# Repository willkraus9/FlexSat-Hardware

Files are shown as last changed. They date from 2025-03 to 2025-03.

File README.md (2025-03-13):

# FlexSat-Hardware

Happy FlexSat

## Hardware Setup:

* Obtain a battery (Turnigy 4S 14.8V 5000mAh, XT90 connector) for each motor

  * There should be another motor assembly in the lab for experiments with the two motor setup.
* Attach assembly to the mocap cage

  * Hold the aluminum plate perpendicular to a column in the mocap cage
  * Loosely fix the pipe clamps around the pipes
  * Tighten the pipe clamps with a Philips Head screwdriver
  * Make sure the final assembly is level, the final fit should be very snug

## Systems Overview:

### Motor Assembly

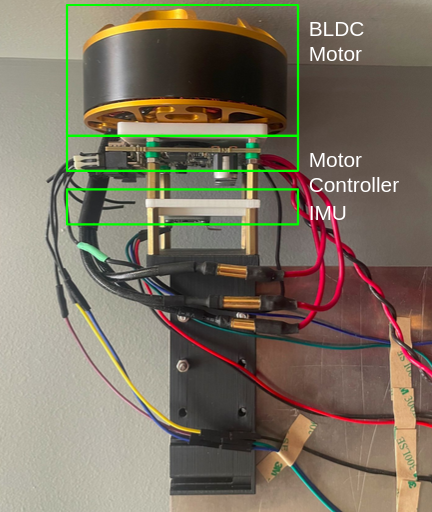
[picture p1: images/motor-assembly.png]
Motor Assembly


* The assembly is held together by M3 screws and standoffs. Reaching components for replacement (such as the motor) or manually adjusting (such as the IMUs) can be done with a small Philips screwdriver
* Ensure that the plastic spacers are attached such that the board does not short circuit due to how close metal components are to the PCB.

### Wiring Assembly

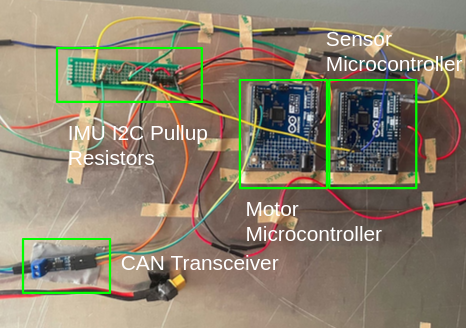
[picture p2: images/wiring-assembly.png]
Happy FlexSat


* Ensure the custom battery connector (XT90 -> XT60) is appropriately attached to the motor controller and the battery is secured
* Ensure the DuPont wires are attached to the microcontrollers and none have fallen out or bent
  * Pin connections can be found in the appropriate .ino files

## Initializing an Experiment:

1. Plug the motor(s) into battery power
2. Plug a computer into the motor controller using a USB type C cable
3. Initialize motor calibration as velocity control and testing using this link: https://gui.odriverobotics.com/

   * This should be done already and save over different sessions. However, testing the motors to check calibration ONLY would be helpful
   * More details for debugging: https://docs.odriverobotics.com/v/latest/interfaces/gui.html
4. Remove the USB cable from the motor controller
5. Attach two separate USB cables to the two separate microcontrollers
6. Test IMU data collection with the file FrequencyScheduler.ino
7. Test motor actuation with MotorTesterSingleArduino.ino, this should not rely on any IMU measurements.

## Running an Experiment:

1. Configure the scripts and USB connections

* MotorDualArduino.ino
* FrequencyScheduler.ino
* HW_Data_Collection.m

  * This file has more information about possible USB port configurations for the corresponding microcontrollers
  * If this is different for the host computer, ensure this matches the USB configuration in the Arduino IDE.

2. Run the experiment

* Ensure the serial port to the MATLAB script holds priority by running this file first

  * Reset both microcontrollers by using the RESET buttons on the boards
  * Data from the IMU measurements will be stored in sysid_array in MATLAB
  * Copy the data and reformat as needed for sysid experiments

## Possible Debugging:

Issue: Motors refuse to calibrate correctly in the ODrive GUI (mismatch in the number of poles on the motor)

* The Hall effect magnet for the onboard encoder is misaligned
* Not enough power is reaching the motor controller
* The motor controller is shorting on metal components of the assembly (unlikely)
* The three cables from the motor are making electrical contact (unlikely)

Issue: The MATLAB script runs for~30 iterations at 100 Hz

* One of the arduinos is not functioning; check MessageHandler.m -> fix arduino
* Also: don't print anything to the serial line when the arduinos are running

Issue: Microcontrollers communication issues with MATLAB

* Close the Arduino IDE, unplug both usb connectors, plug the cables back in, then run the MATLAB script

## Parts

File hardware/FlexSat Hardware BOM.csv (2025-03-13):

 | Name | Quantity | Link (if needed) | Description
Mechanical Parts
Aluminum 6061 Plate | Aluminum Plate | 1 | N/A | Dimensions: 3.175mm x 304.8mm x 1.2192m
Motor Assembly (3D Printed) | Plate to IMU Bracket | 2 | N/A | Holds Motor Assembly onto plate
 | IMU Bracket | 2 | N/A | Holds IMUs in place with adjustable orientation
 | Motor Bracket | 2 | N/A | Holds IMUs in place with adjustable orientation
Mocap Cage Attachment Assembly | Aluminum Extrusion | 4 | N/A | Secures aluminum plate to attachment assembly
 | Angle Bracket | 4 | https://www.amazon.com/Corner-Brackets-Aluminum-Extrusion-Profile/dp/B09YQ3KSC4 | Screw mounts for attachment assembly
 | Pipe Clamp | 4 | https://www.grainger.com/product/NVENT-CADDY-Pipe-Clamp-Swivel-Loop-1RVC5 | Secures attachment assembly to mocap cage
 | Angle Plate | 4 | N/A | N/A
Miscellaneous | Encoder Magnet | 1 | N/A | Magnet for Hall Effect encoder
Electronic Parts
Motor Control | Arduino Uno R4 Minima | 1 | https://www.amazon.com/dp/B0C78K4CD4?psc=1&ref=ppx_yo2ov_dt_b_product_details | Microcontroller for receiving data and sending motor commands
 | Waveshare SN65HVD230 | 1 | https://www.amazon.com/dp/B0B5DTN62K?psc=1&ref=ppx_yo2ov_dt_b_product_details | CAN Transceiver
 | ODrive Pro | 1 | https://odriverobotics.com/shop/odrive-pro | Motor control board
 | Herlea X8318S KV100 | 1 | https://www.aliexpress.us/item/3256805690296061.html?src=google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 | Brushless DC motor for reaction wheel
IMU | BNO055 | 2 | https://adafruit.com/product/2472 | IMU
Miscellaneous | Breadboard | 1 | N/A | Additional wiring support
 | USB Type C - USB Cable | 1 | N/A | Upload cable to microcontroller

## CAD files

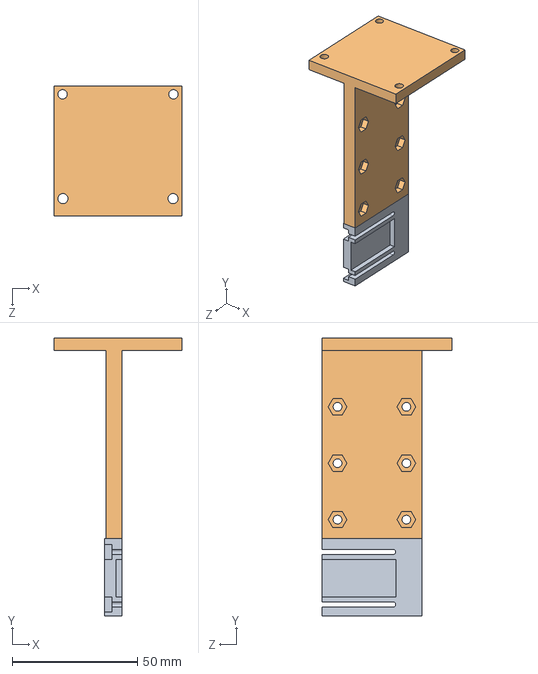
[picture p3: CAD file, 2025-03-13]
hardware/3D Printed Parts/RExFLEx_Omnis.SLDASM
51.0 x 111.0 x 52.0 mm
RExFLEx_IMU_Sleeve2
RExFLEx_IMU_Sleeve_2

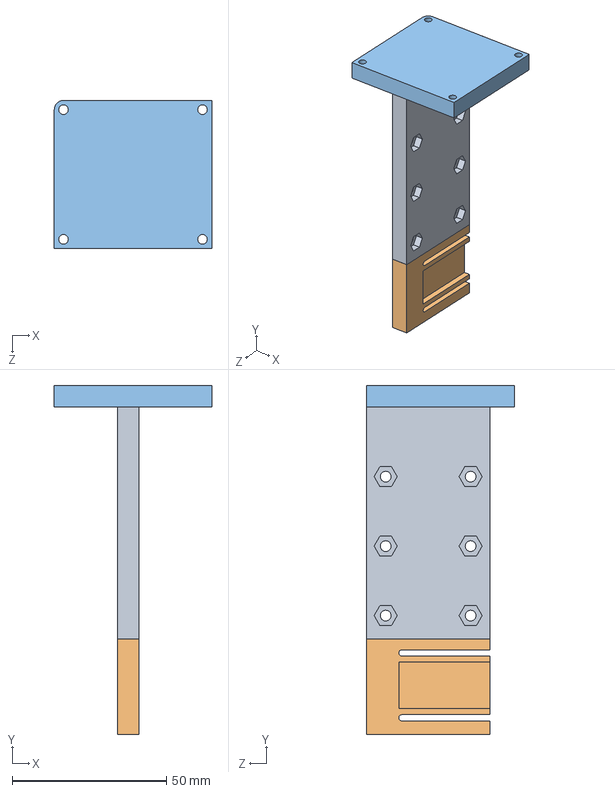
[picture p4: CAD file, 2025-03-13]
hardware/3D Printed Parts/Aluminum Mount/RExFlex_Sleeve_Final.SLDASM
51.0 x 113.0 x 48.0 mm
RExFLEx_Screws_Final
IMU_Sleeve_Final
RExFLEx_Controller_Final

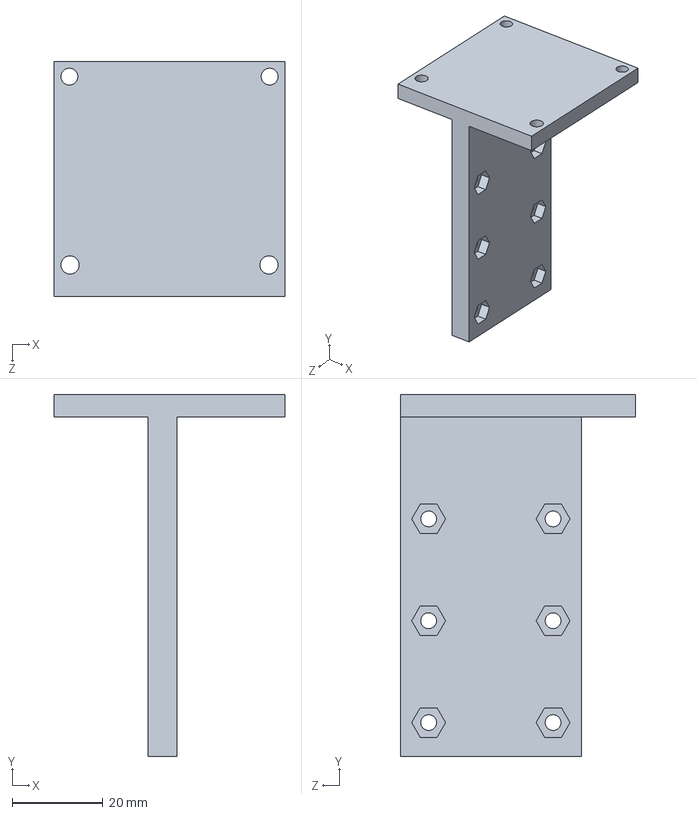
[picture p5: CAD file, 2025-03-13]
hardware/3D Printed Parts/Aluminum Mount/RExFLEx_Sleeve.SLDPRT
51.0 x 80.0 x 52.0 mm

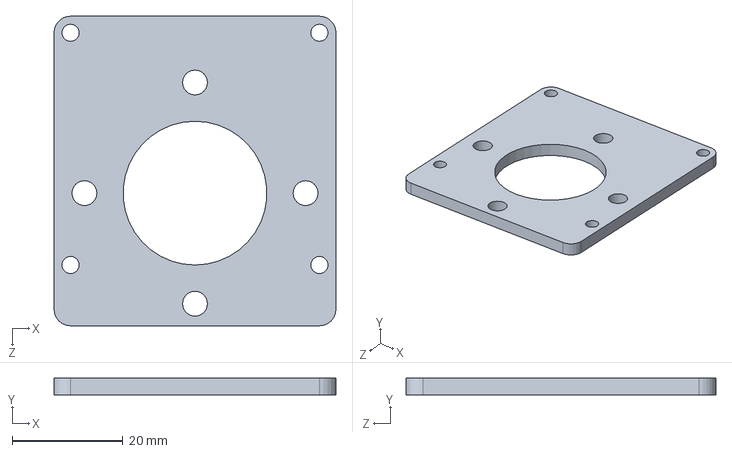
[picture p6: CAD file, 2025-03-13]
hardware/3D Printed Parts/BLDC Mount/RExFLEx_Motor.SLDPRT
51.0 x 3.00 x 56.0 mm

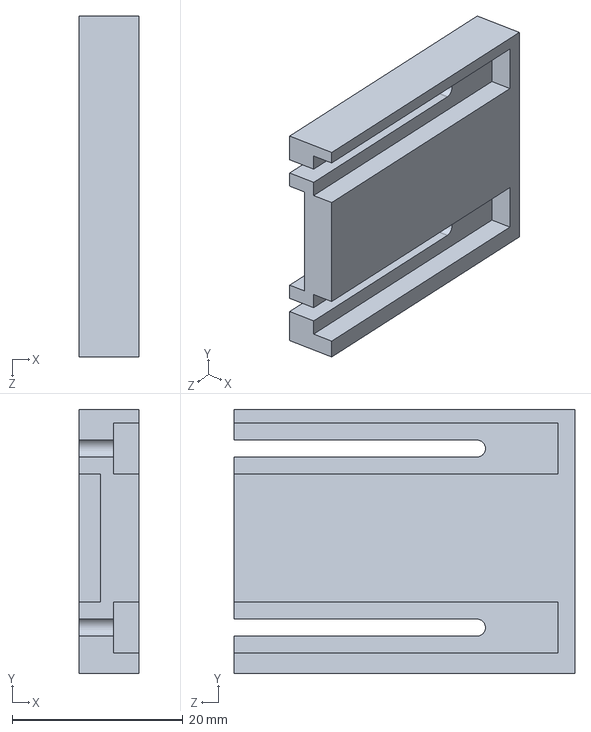
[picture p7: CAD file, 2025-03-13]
hardware/3D Printed Parts/IMU Mount/IMU_Sleeve_Plate.SLDPRT
7.00 x 31.0 x 40.0 mm

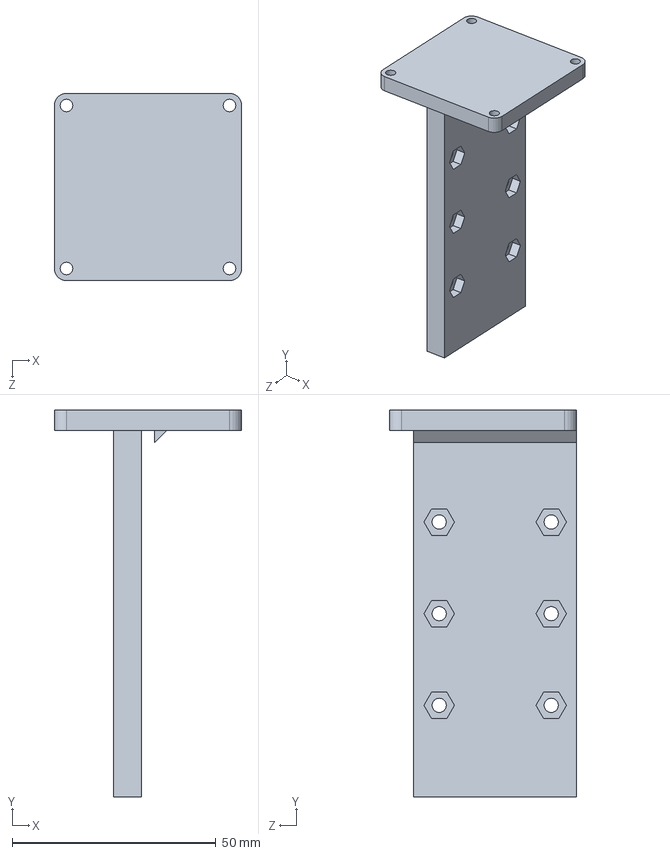
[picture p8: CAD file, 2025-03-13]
hardware/3D Printed Parts/Aluminum Mount/REx Beam Sleeve5.SLDPRT
46.0 x 95.0 x 46.0 mm

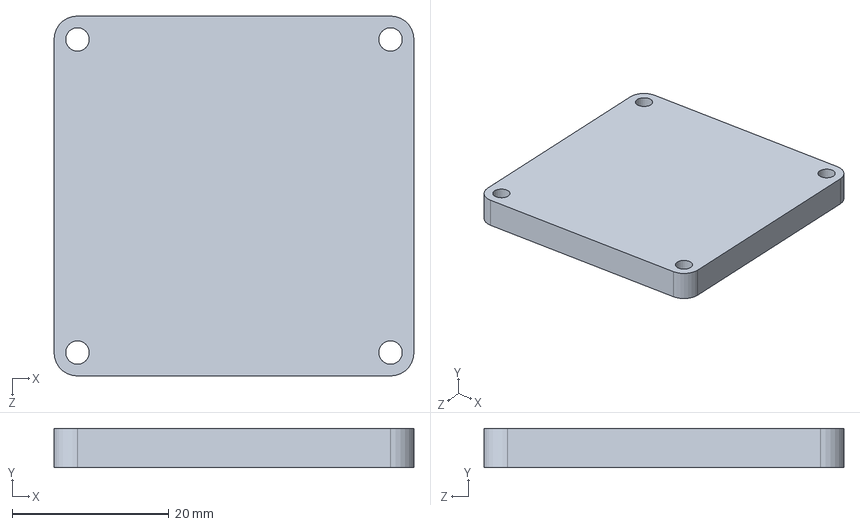
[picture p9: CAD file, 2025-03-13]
hardware/3D Printed Parts/BLDC Mount/RExFLEx_Board.SLDPRT
46.0 x 5.00 x 46.0 mm

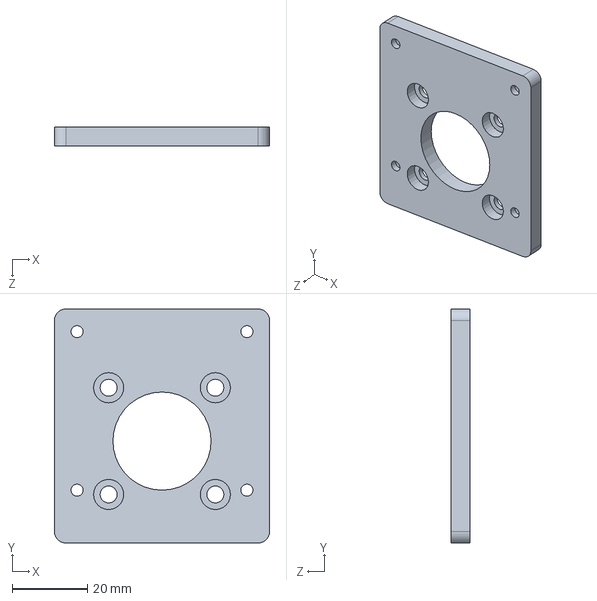
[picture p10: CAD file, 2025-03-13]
hardware/3D Printed Parts/BLDC Mount/RExFLEx_Motor2.SLDPRT
57.0 x 62.0 x 5.00 mm

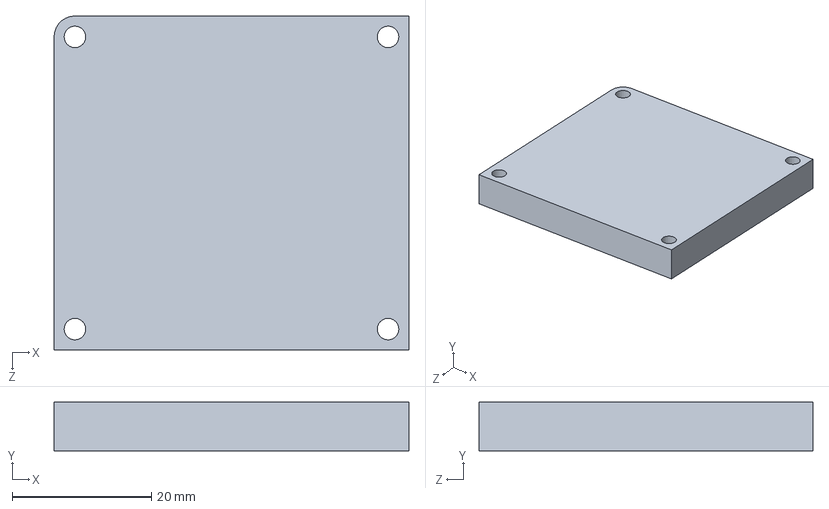
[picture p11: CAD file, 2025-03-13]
hardware/3D Printed Parts/BLDC Mount/RExFLEx_Controller_Final.SLDPRT
51.0 x 7.00 x 48.0 mm

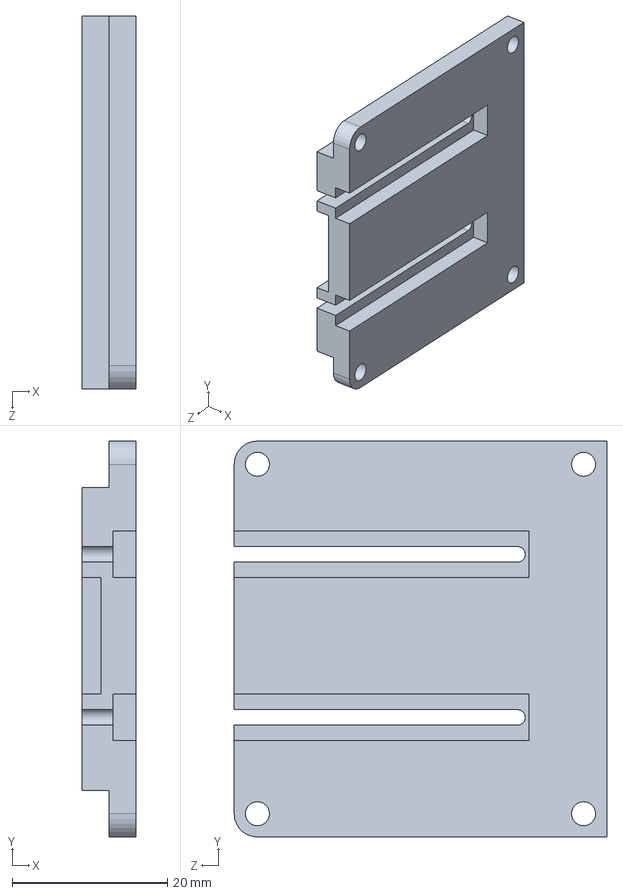
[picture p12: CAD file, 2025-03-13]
hardware/3D Printed Parts/IMU Mount/IMU_Plate2.SLDPRT
7.00 x 51.0 x 48.0 mm

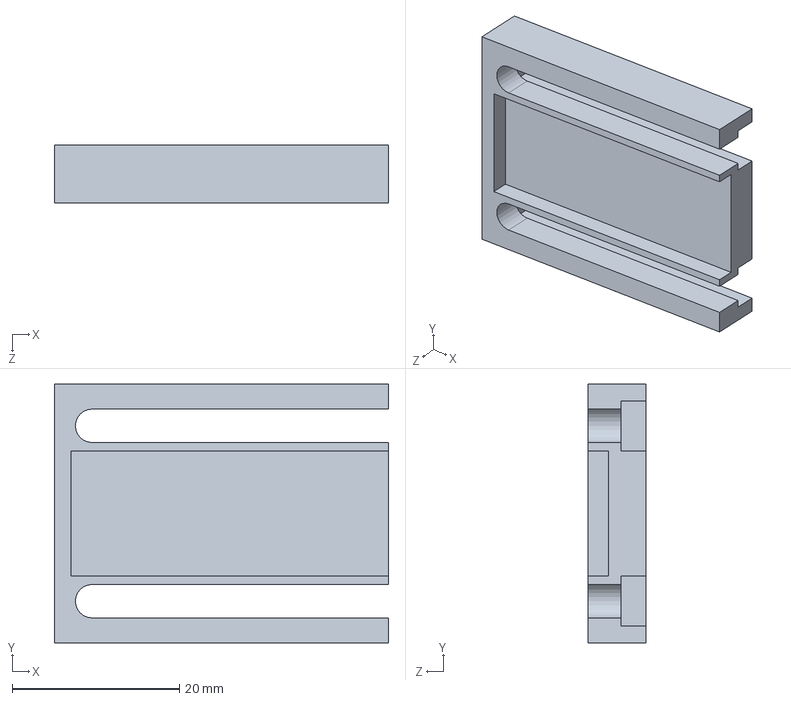
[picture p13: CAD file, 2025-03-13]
hardware/3D Printed Parts/IMU Mount/IMU_Mount_1.SLDPRT
40.0 x 31.0 x 7.00 mm

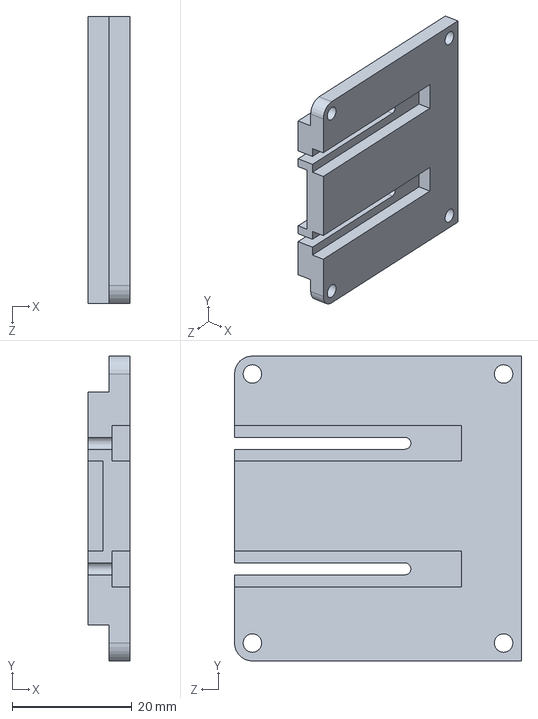
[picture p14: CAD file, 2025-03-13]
hardware/3D Printed Parts/IMU Mount/IMU_Plate.SLDPRT
7.00 x 51.0 x 48.0 mm

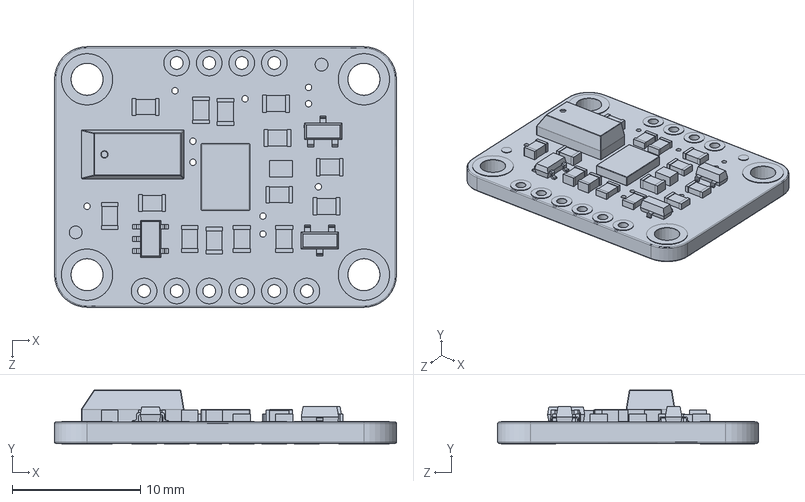
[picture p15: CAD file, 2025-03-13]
hardware/3D Printed Parts/IMU Mount/Adafruit_BNO055.SLDPRT
26.7 x 4.20 x 20.3 mm

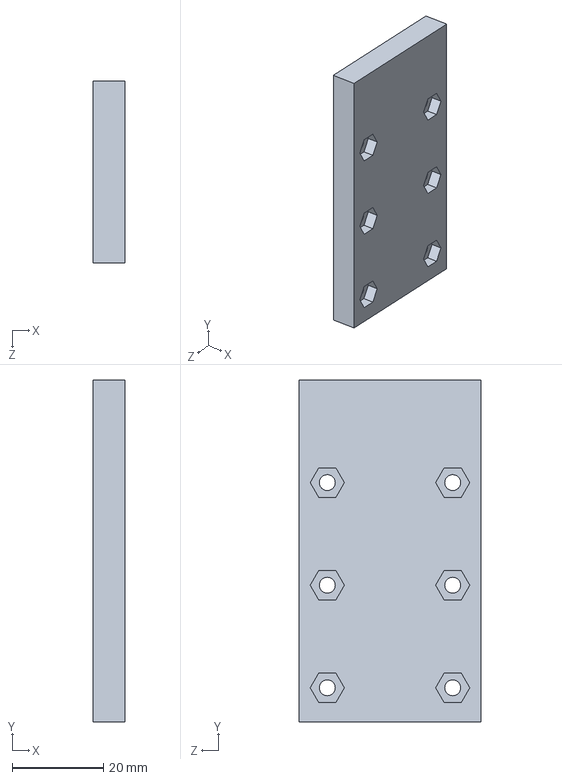
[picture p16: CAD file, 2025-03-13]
hardware/3D Printed Parts/RExFLEx_Screws_Final.SLDPRT
7.00 x 75.0 x 40.0 mm

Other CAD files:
hardware/3D Printed Parts/IMU Mount/RExFLEx_IMU_Sleeve.SLDASM
hardware/3D Printed Parts/IMU Mount/RExFLEx_IMU_Sleeve2.SLDPRT
hardware/3D Printed Parts/IMU Mount/IMU_Sleeve_Final.SLDPRT
hardware/3D Printed Parts/IMU Mount/RExFLEx_IMU_Sleeve_ODRIVE.SLDPRT
hardware/3D Printed Parts/Aluminum Mount/RExFlex_Sleeve_Final.SLDPRT
hardware/3D Printed Parts/Aluminum Mount/RExFlex_Sleeve_Final.STL
hardware/3D Printed Parts/BLDC Mount/RExFLEx_Motor.STL
hardware/3D Printed Parts/BLDC Mount/RExFLEx_Motor2.STL
hardware/3D Printed Parts/IMU Mount/IMU_Plate.STL
hardware/3D Printed Parts/IMU Mount/IMU_Plate2.STL
hardware/3D Printed Parts/IMU Mount/RExFLEx_IMU_Sleeve.SLDPRT
hardware/3D Printed Parts/IMU Mount/RExFLEx_IMU_Sleeve.STL
hardware/3D Printed Parts/IMU Mount/RExFLEx_IMU_Sleeve2.3mf
hardware/3D Printed Parts/IMU Mount/RExFLEx_IMU_Sleeve_2.SLDPRT

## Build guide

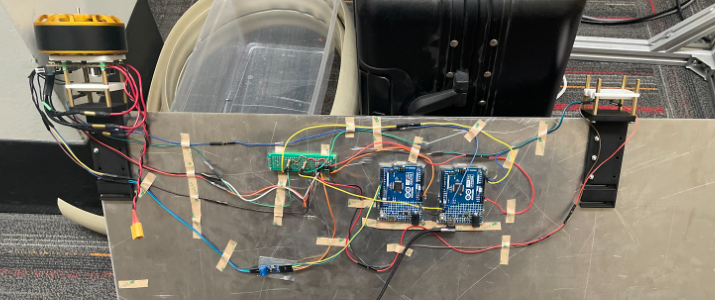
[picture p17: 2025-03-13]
images/whole-assembly.png

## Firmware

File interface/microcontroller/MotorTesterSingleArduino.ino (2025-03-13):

#include <Arduino.h>
#include "ODriveCAN.h"
#include <Arduino_CAN.h>
#include <ODriveHardwareCAN.hpp>
// Documentation for this example can be found here:
// https://docs.odriverobotics.com/v/latest/guides/arduino-can-guide.html
// See https://github.com/arduino/ArduinoCore-API/blob/master/api/HardwareCAN.h
// and https://github.com/arduino/ArduinoCore-renesas/tree/main/libraries/Arduino_CAN

// TIMING ===========================================================================================================
int n = 0;
unsigned long ttimee = 0;
int motorValue = 0;
const int DATA_SIZE = 300; // NB: unsure if need this, from when IMU used 

// RW Setup for pseudorandom signal
float rampValue; // value sent to motor during ramp 
float rampTime; // time start ramping value

float randomValue; // value sent to motor during random actuation 
float randomTime; // time start random actuation

float velValue; // actual velocity command for motor

// RW Setup for chirp signal
const int f0 = 0.1; // minimum frequency
const int f1 = 10.0; // maximum frequency, changed to focus on lower frequencies
const float T = 180.0; //duration of signal (180 seconds)
const float Fs = 50.0; // frequency for data collection
const unsigned long samplePeriod = 1000000 / Fs;  // Sample period (microseconds)

unsigned long lastSampleTime = 0;

// CAN bus baudrate. Make sure this matches for every device on the bus
#define CAN_BAUDRATE 250000
// ODrive node_id for odrv0
#define ODRV0_NODE_ID 0
#define IS_ARDUINO_BUILTIN // Arduino boards with built-in CAN interface (e.g. Arduino Uno R4 Minima)
HardwareCAN& can_intf = CAN;
bool setupCan() {
  return can_intf.begin((CanBitRate)CAN_BAUDRATE);
}

// Instantiate ODrive objects
ODriveCAN odrv0(wrap_can_intf(can_intf), ODRV0_NODE_ID); // Standard CAN message ID
ODriveCAN* odrives[] = {&odrv0}; // Make sure all ODriveCAN instances are accounted for here

struct ODriveUserData {
  Heartbeat_msg_t last_heartbeat;
  bool received_heartbeat = false;
  Get_Encoder_Estimates_msg_t last_feedback;
  bool received_feedback = false;
};

// Keep some application-specific user data for every ODrive.
ODriveUserData odrv0_user_data;

// Called every time a Heartbeat message arrives from the ODrive
void onHeartbeat(Heartbeat_msg_t& msg, void* user_data) {
  ODriveUserData* odrv_user_data = static_cast<ODriveUserData*>(user_data);
  odrv_user_data->last_heartbeat = msg;
  odrv_user_data->received_heartbeat = true;
}

// Called every time a feedback message arrives from the ODrive
void onFeedback(Get_Encoder_Estimates_msg_t& msg, void* user_data) {
  ODriveUserData* odrv_user_data = static_cast<ODriveUserData*>(user_data);
  odrv_user_data->last_feedback = msg;
  odrv_user_data->received_feedback = true;
}

// Called for every message that arrives on the CAN bus
void onCanMessage(const CanMsg& msg) {
  for (auto odrive: odrives) {
    onReceive(msg, *odrive);
  }
}

void setup() {
  Serial.begin(115200);
  // Wait for up to 3 seconds for the serial port to be opened on the PC side.
  // If no PC connects, continue anyway.
  for (int i = 0; i < 30 && !Serial; ++i) {
    delay(100);
  }
  delay(200);

  Serial.println("Starting ODriveCAN demo");

  // Register callbacks for the heartbeat and encoder feedback messages
  odrv0.onFeedback(onFeedback, &odrv0_user_data);
  odrv0.onStatus(onHeartbeat, &odrv0_user_data);

  // Configure and initialize the CAN bus interface. This function depends on
  // your hardware and the CAN stack that you're using.
  if (!setupCan()) {
    Serial.println("CAN failed to initialize: reset required");
    while (true); // spin indefinitely
  }

  Serial.println("Waiting for ODrive...");
  while (!odrv0_user_data.received_heartbeat) {
    pumpEvents(can_intf);
    delay(100);
  }

  Serial.println("found ODrive");

  // request bus voltage and current (1sec timeout)
  Serial.println("attempting to read bus voltage and current");
  Get_Bus_Voltage_Current_msg_t vbus;
  if (!odrv0.request(vbus, 1)) {
    Serial.println("vbus request failed!");
    while (true); // spin indefinitely
  }

  Serial.print("DC voltage [V]: ");
  Serial.println(vbus.Bus_Voltage);
  Serial.print("DC current [A]: ");
  Serial.println(vbus.Bus_Current);

  Serial.println("Enabling closed loop control...");
  while (odrv0_user_data.last_heartbeat.Axis_State != ODriveAxisState::AXIS_STATE_CLOSED_LOOP_CONTROL) {
    odrv0.clearErrors();
    delay(1);
    odrv0.setState(ODriveAxisState::AXIS_STATE_CLOSED_LOOP_CONTROL);
    // Pump events for 150ms. This delay is needed for two reasons;
    // 1. If there is an error condition, such as missing DC power, the ODrive might
    //    briefly attempt to enter CLOSED_LOOP_CONTROL state, so we can't rely
    //    on the first heartbeat response, so we want to receive at least two
    //    heartbeats (100ms default interval).
    // 2. If the bus is congested, the setState command won't get through
    //    immediately but can be delayed.
    for (int i = 0; i < 15; ++i) {
      delay(10);
      pumpEvents(can_intf);
    }
  }
  Serial.println("ODrive running!");
}
void loop() {
  unsigned long currentTime = micros(); //only read micros() once  
  pumpEvents(can_intf); // This is required on some platforms to handle incoming feedback CAN messages
  rampValue = (currentTime / 1000000) - rampTime;
    // should go from 0 to middle of randomValue's range (manually set)
    // currentTime in seconds - rampTime (0 at 10, 1 at 11, 2 at 12, etc.; do until reach end)
  rampTime = 30;
  randomValue = random(10,21); // hard limit is (-25, 25) rotations per second; 
    // hardware bug: anything above 15 rad/s may cause the IMUs to stop sending data
    // NB: random() excludes the second value for the range!
  randomTime = rampTime + 16; // ensures in between random values 
  if (currentTime / 1000000 < rampTime) {// (30 seconds aka 30,000,000 microseconds) (this is for getting a standard bias term)
    velValue = 0;
    } else if (currentTime / 1000000 > rampTime && currentTime / 1000000 < randomTime){
    velValue = 0; // no ramp value since torque control!
    } else if (currentTime / 1000000 > randomTime){
      float t = (currentTime / 1000000.0);  // Convert time to seconds
      float k = (f1 - f0) / T;
      float chirpFreq = f0 + k * t;
      float chirpSignal = 0.5 * (sin(2 * PI * chirpFreq * t));
      velValue = chirpSignal*1.5; // should be -0.1 to 0.1 --> chirpSignal*2
    }
    odrv0.setTorque(velValue);
    Serial.println(velValue);
}
// Troubleshooting: 
// The IMUs aren't connecting: unplug the Arduino, double tap the RESET button, and run the code again. Check imu_bus_tester to see if the IMUs are being read.
// This script runs and nothing gets printed to the command line: this is an issue with the Arduino. Double tap the RESET button, power cycle the Arduino, and run the script again. 

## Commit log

2025-03-13 Added images
    [Adafruit_BNO055.SLDPRT, FlexSat Hardware BOM.csv, IMU_Mount_1.SLDPRT, IMU_Plate.SLDPRT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]
2025-03-13 Added scripts, better README
    [_100mm_90seconds.csv]
